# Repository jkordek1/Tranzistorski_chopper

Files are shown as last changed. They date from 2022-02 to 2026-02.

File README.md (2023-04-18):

# Tranzistorski_chopper


[]()



## O projektu
 Tranzistorski chopper korišten za laboratorijske vježbe na elektrotehničkom odjelu TVZ-a.
 
 ## Značajke
 - Ulazni napon do 24V
 - Potenciometar za promjenu širine impulsa visokog stanja PWM-a
 - Ušice za sonde osciloskopa
 - 3 različite frekvencije PWM-a koje se odabiru pomoću kratkospojnika
 
 ## Slike
<p align="center">
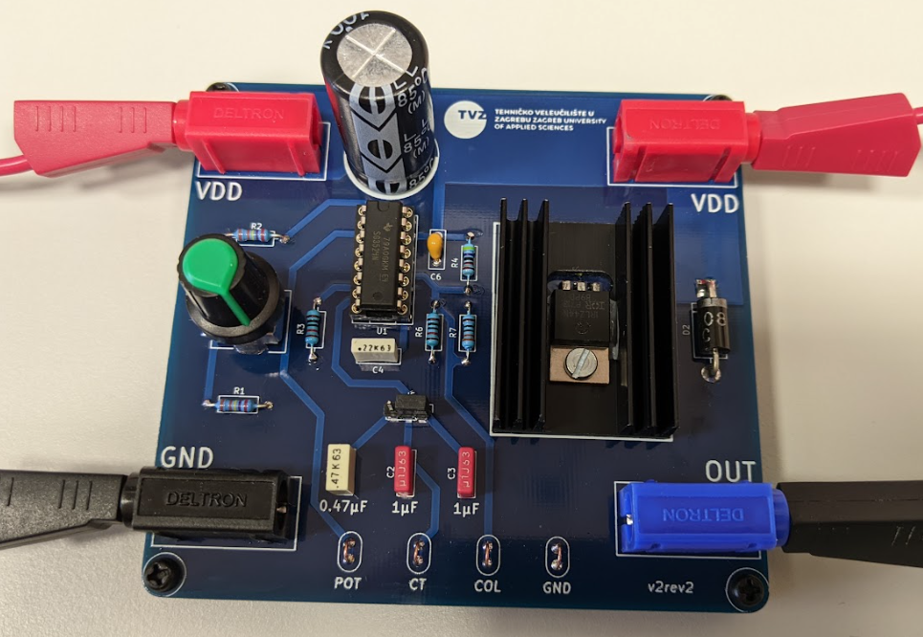
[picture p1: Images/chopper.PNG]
 
</p>

## Struktura mape
    .
    ├── ...
    ├── 3d modeli               # 3d modeli komponenata
    ├── Images                  # Slike i grafički elementi dodani na pločicu
    ├── KiCad files             # Glavna mapa KiCAD projekta
    │   ├── Board2Pdf           # Montažna shema
    │   ├── bom                 # ibom pomoćna datoteka za montažu komponenata
    │   ├── Dokumentacija       # Električna shema
    │   ├── gerber              # gerber mapa
    │   └── Slike               # 3D render sklopa
    └── ...

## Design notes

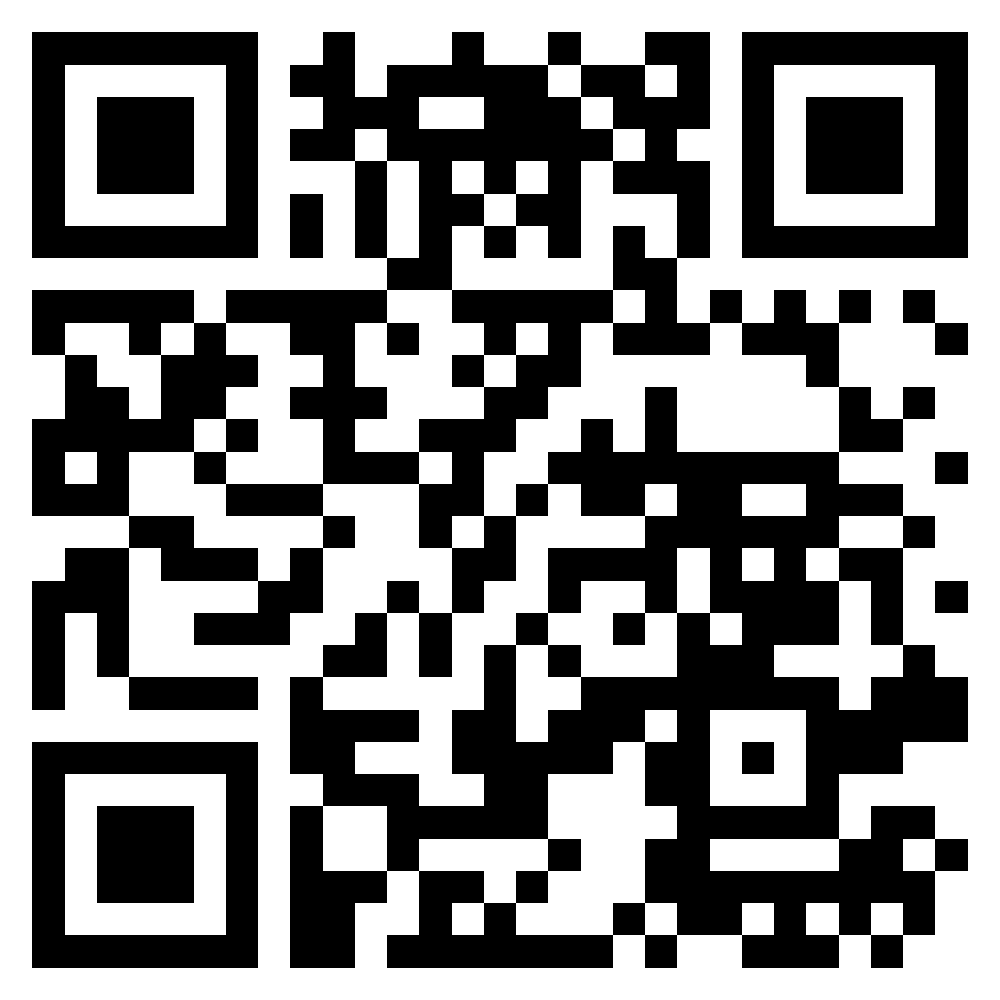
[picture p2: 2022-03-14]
Images/qr.png

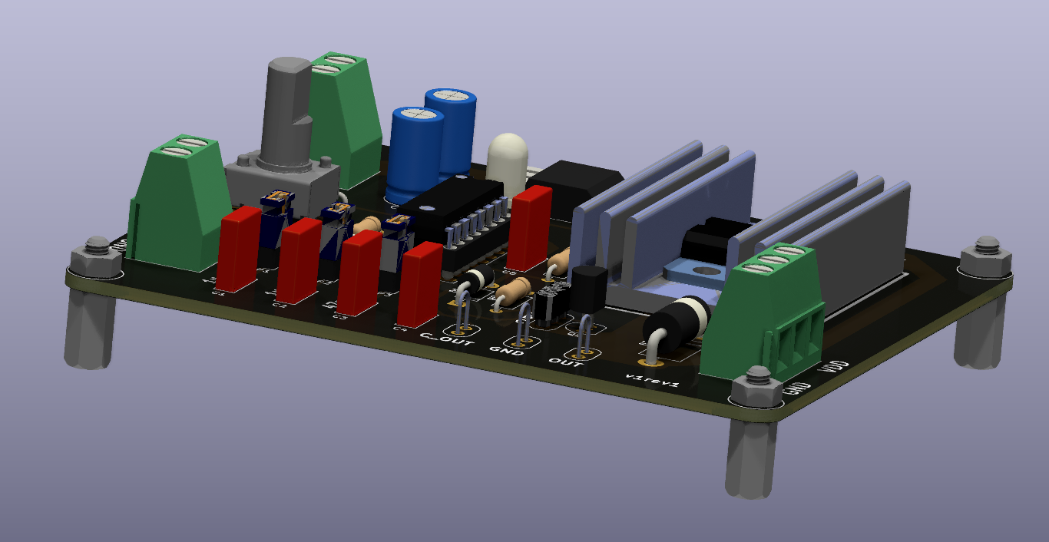
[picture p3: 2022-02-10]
KiCad files/Slike/render.PNG

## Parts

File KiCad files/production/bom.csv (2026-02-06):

Designator | Footprint | Quantity | Value | LCSC Part #
B1, B3 | DELTRON 4mm banana socket - red | 2 | Screw_Terminal_01x01
B2, B4 | DELTRON 4mm banana socket - black | 2 | Screw_Terminal_01x01
C1 | C_Rect_L7.2mm_W2.5mm_P5.00mm_FKS2_FKP2_MKS2_MKP2 | 1 | 1uF
C2 | C_Rect_L7.2mm_W2.5mm_P5.00mm_FKS2_FKP2_MKS2_MKP2 | 1 | 0.47uF
C3 | C_Rect_L7.2mm_W2.5mm_P5.00mm_FKS2_FKP2_MKS2_MKP2 | 1 | 0.22uF
C4 | C_Rect_L7.2mm_W2.5mm_P5.00mm_FKS2_FKP2_MKS2_MKP2 | 1 | 220n
C5 | CP_Radial_D17.0mm_P7.50mm | 1 | 1000u
C6 | C_Rect_L7.2mm_W2.5mm_P5.00mm_FKS2_FKP2_MKS2_MKP2 | 1 | 100n
D2 | D_DO-201AD_P15.24mm_Horizontal | 1 | 1N5408
H1, H2, H3, H4 | MountingHole_3.2mm_M3 | 4 | MountingHole
J1, J2, J3, J4 | oscil | 4 | Conn_01x01_Male
J5 | PinHeader_1x03_P2.54mm_Vertical | 1 | Conn_01x03_Male
Q1 | TO-220F-3_Horizontal_TabDown | 1 | IRFZ44N
R1 | R_Axial_DIN0207_L6.3mm_D2.5mm_P10.16mm_Horizontal | 1 | 3k3
R2 | R_Axial_DIN0207_L6.3mm_D2.5mm_P10.16mm_Horizontal | 1 | 4k7
R3 | R_Axial_DIN0207_L6.3mm_D2.5mm_P10.16mm_Horizontal | 1 | 2k2
R4, R6 | R_Axial_DIN0207_L6.3mm_D2.5mm_P10.16mm_Horizontal | 2 | 10k
R7 | R_Axial_DIN0207_L6.3mm_D2.5mm_P10.16mm_Horizontal | 1 | 330
RV1 | PTV09A-4225F-B502 | 1 | 10k
U1 | DIP-16_W7.62mm_Socket_LongPads | 1 | SG3524

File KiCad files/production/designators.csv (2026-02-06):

B1:1
B2:1
B3:1
B4:1
C1:1
C2:1
C3:1
C4:1
C5:1
C6:1
D2:1
G***:3
H1:1
H2:1
H3:1
H4:1
J1:1
J2:1
J3:1
J4:1
J5:1
Q1:1
R1:1
R2:1
R3:1
R4:1
R6:1
R7:1
RV1:1
U1:1

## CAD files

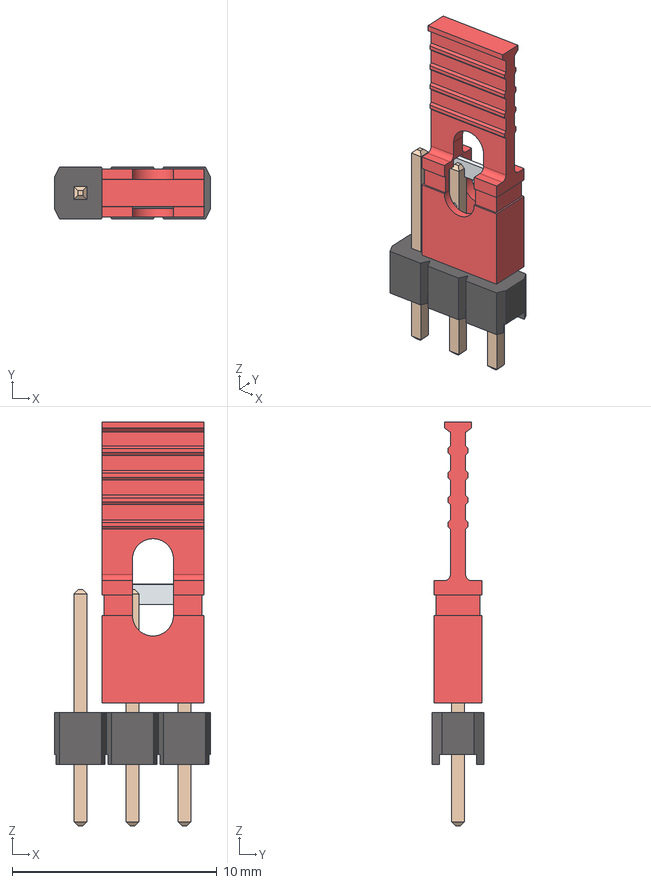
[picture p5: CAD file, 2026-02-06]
3d modeli/pinheader 1x3 and 1 jumper pullback.stp
7.62 x 2.54 x 19.7 mm

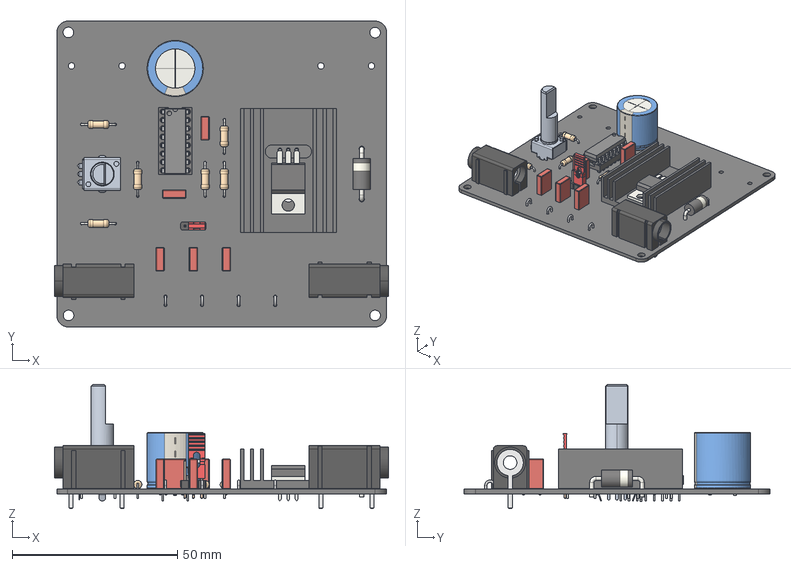
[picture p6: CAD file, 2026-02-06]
KiCad files/Tranzistorski_pretvarač.step
101.1 x 92.6 x 37.5 mm
R_Axial_DIN0207_L6.3mm_D2.5mm_P10.16mm_Horizontal x 6
C_Rect_L7.2mm_W2.5mm_P5.00mm_FKS2_FKP2_MKS2_MKP2 x 5
AB2_90DEG_4MM_JACK_PTH-BLK x 2
AB2_90DEG_4MM_JACK_PTH-RED x 2
Tranzistorski_pretvara_ 1.7.1
usica x 4
D_DO-201AD_P15.24mm_Horizontal
TO-220-3_Horizontal_TabDown
Hladnjak
CP_Radial_D17.0mm_P7.50mm
pinheader 1x3 and 1 jumper pullback
DIP-16_W7.62mm_Socket
DIP-16 N
Tranzistorski_pretvaraÄ_PCB

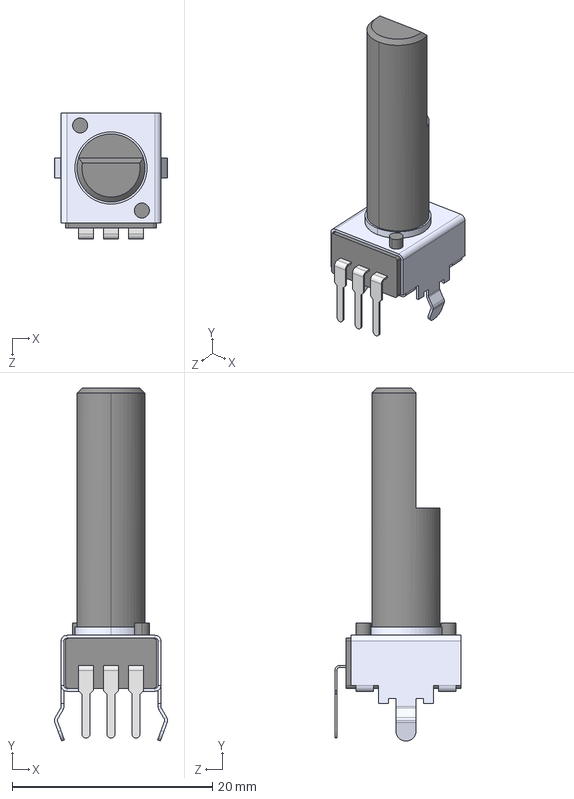
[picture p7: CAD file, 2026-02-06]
3d modeli/PTV09A-4.STEP
11.3 x 35.3 x 12.6 mm
______1.STEP
______2.STEP
______3.STEP

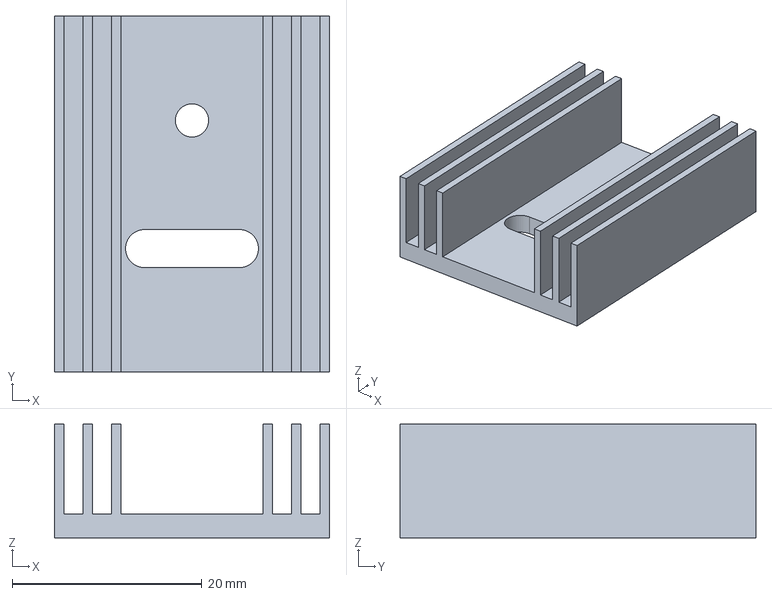
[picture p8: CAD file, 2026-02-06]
3d modeli/Hladnjak.step
29.0 x 37.5 x 12.0 mm

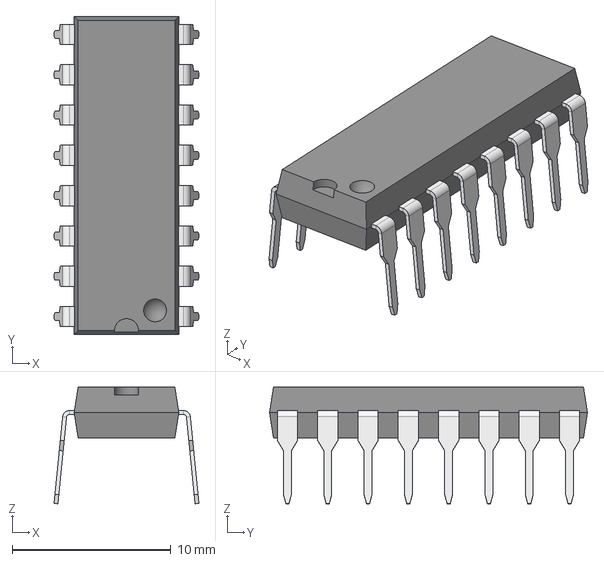
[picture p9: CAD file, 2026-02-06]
3d modeli/DIP-16 N.step
9.14 x 20.0 x 7.35 mm

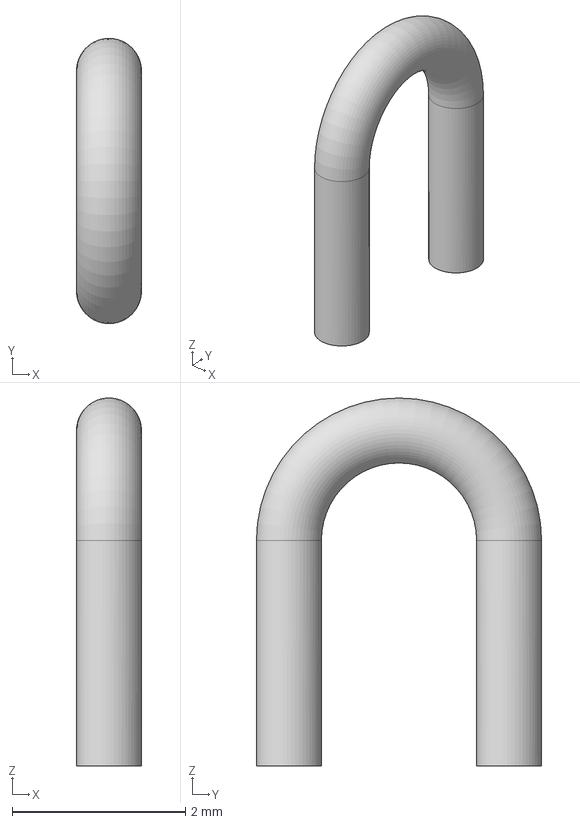
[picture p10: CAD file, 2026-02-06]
3d modeli/usica.step
0.75 x 3.29 x 4.24 mm

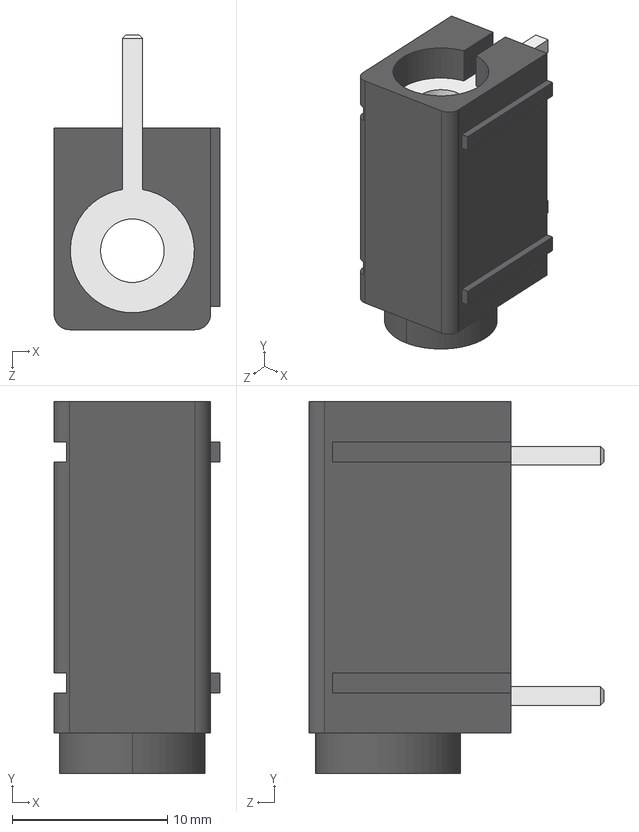
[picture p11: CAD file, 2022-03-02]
3d modeli/AB2_90DEG_4MM_JACK_PTH-BLK.STEP
10.7 x 24.0 x 19.0 mm

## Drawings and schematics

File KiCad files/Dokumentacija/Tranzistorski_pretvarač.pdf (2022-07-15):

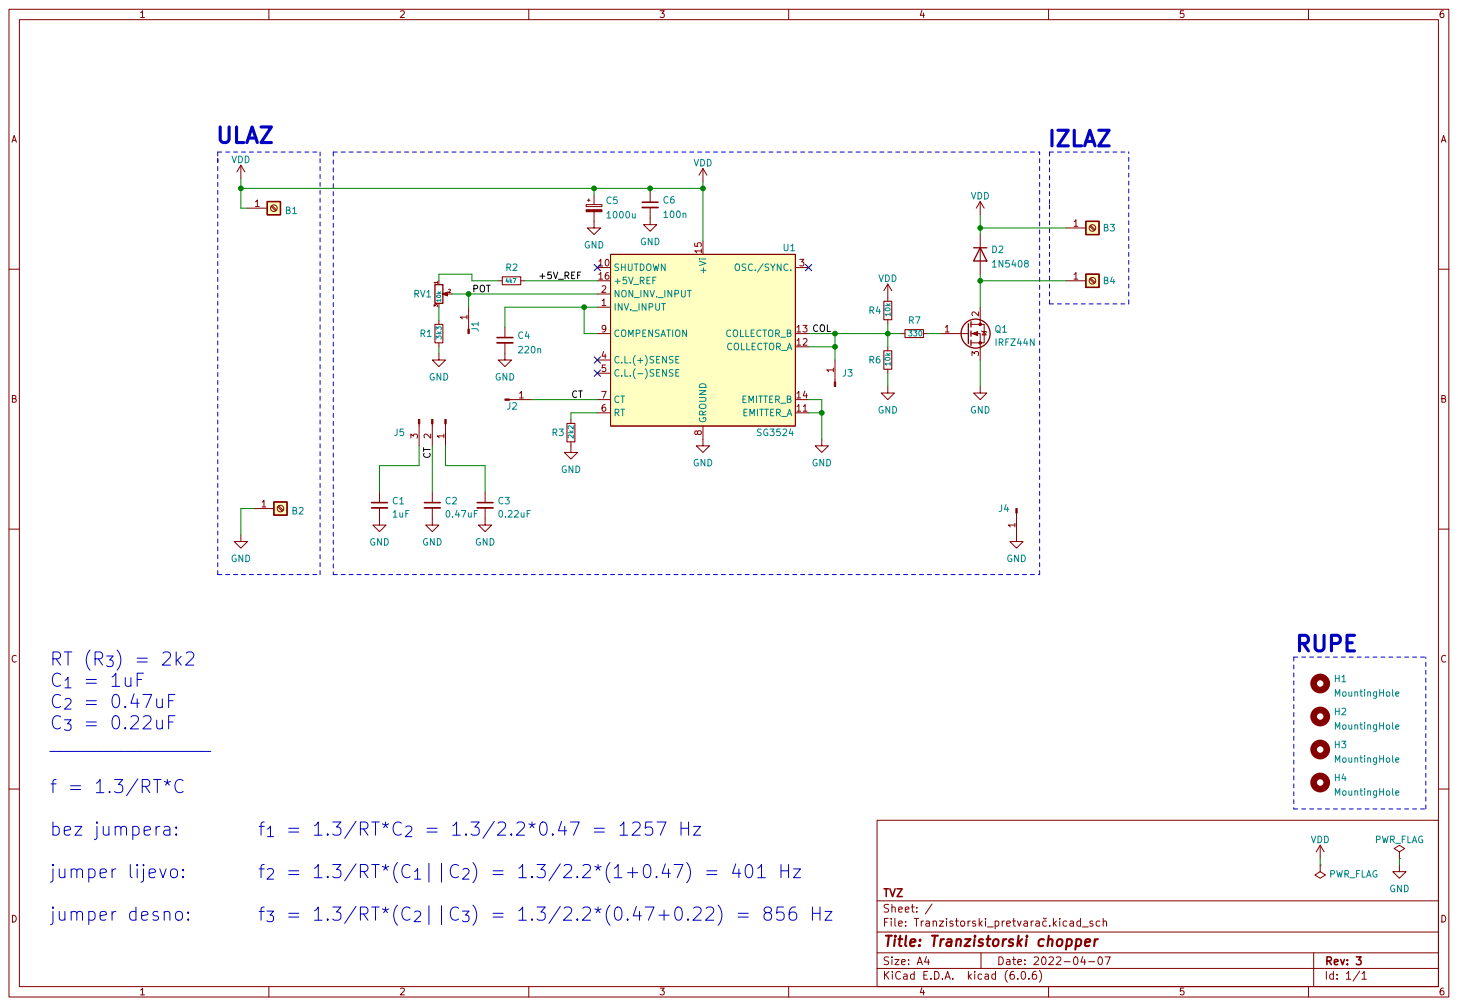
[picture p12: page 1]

bez jumpera: f_{1} = 1.3/RT*C_{2} = 1.3/2.2*0.47 = 1257 Hz

jumper lijevo: f_{2} = 1.3/RT*(C_{1}||C_{2}) = 1.3/2.2*(1+0.47) = 401 Hz

jumper desno: f_{3} = 1.3/RT*(C_{2}||C_{3}) = 1.3/2.2*(0.47+0.22) = 856 Hz

Id: 1/1 Title: Tranzistorski chopper

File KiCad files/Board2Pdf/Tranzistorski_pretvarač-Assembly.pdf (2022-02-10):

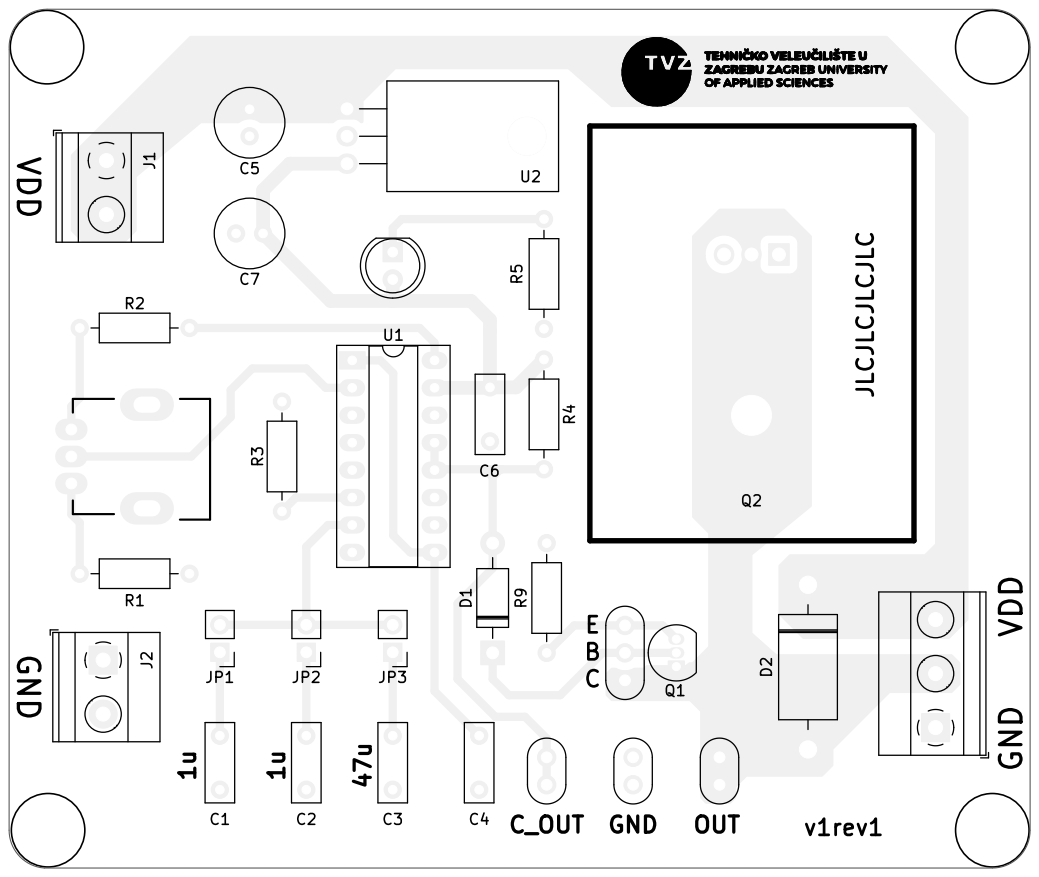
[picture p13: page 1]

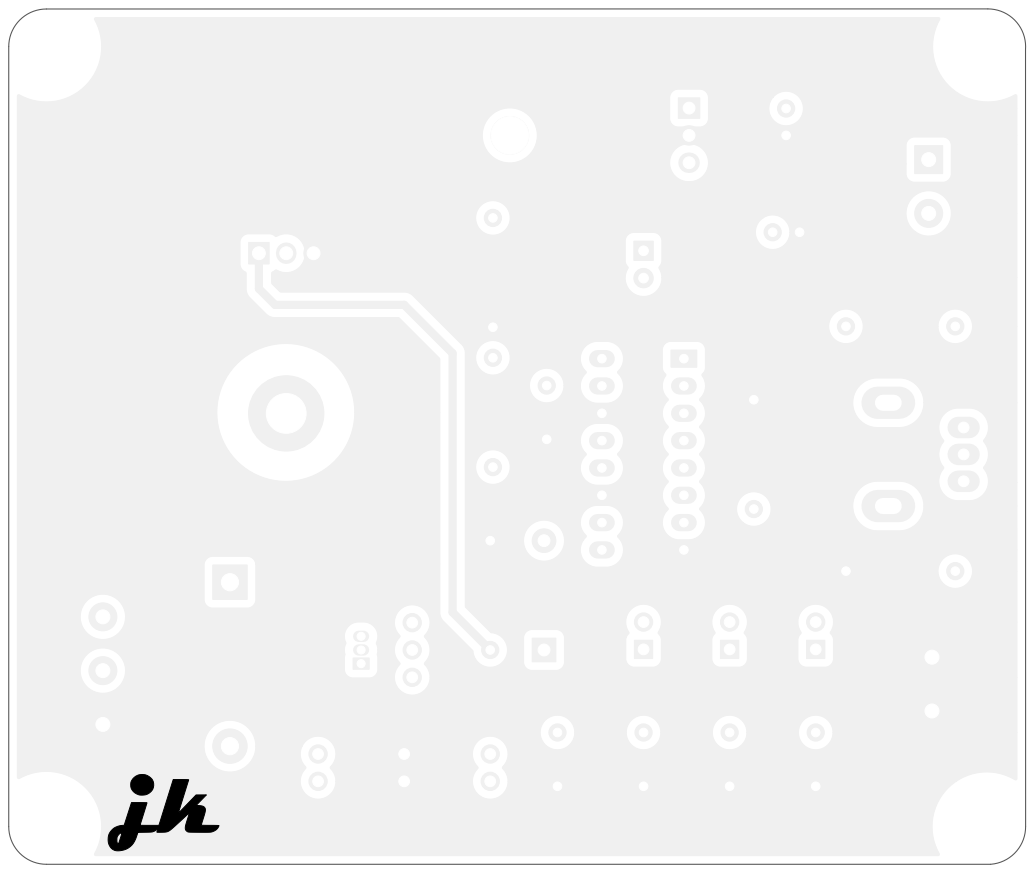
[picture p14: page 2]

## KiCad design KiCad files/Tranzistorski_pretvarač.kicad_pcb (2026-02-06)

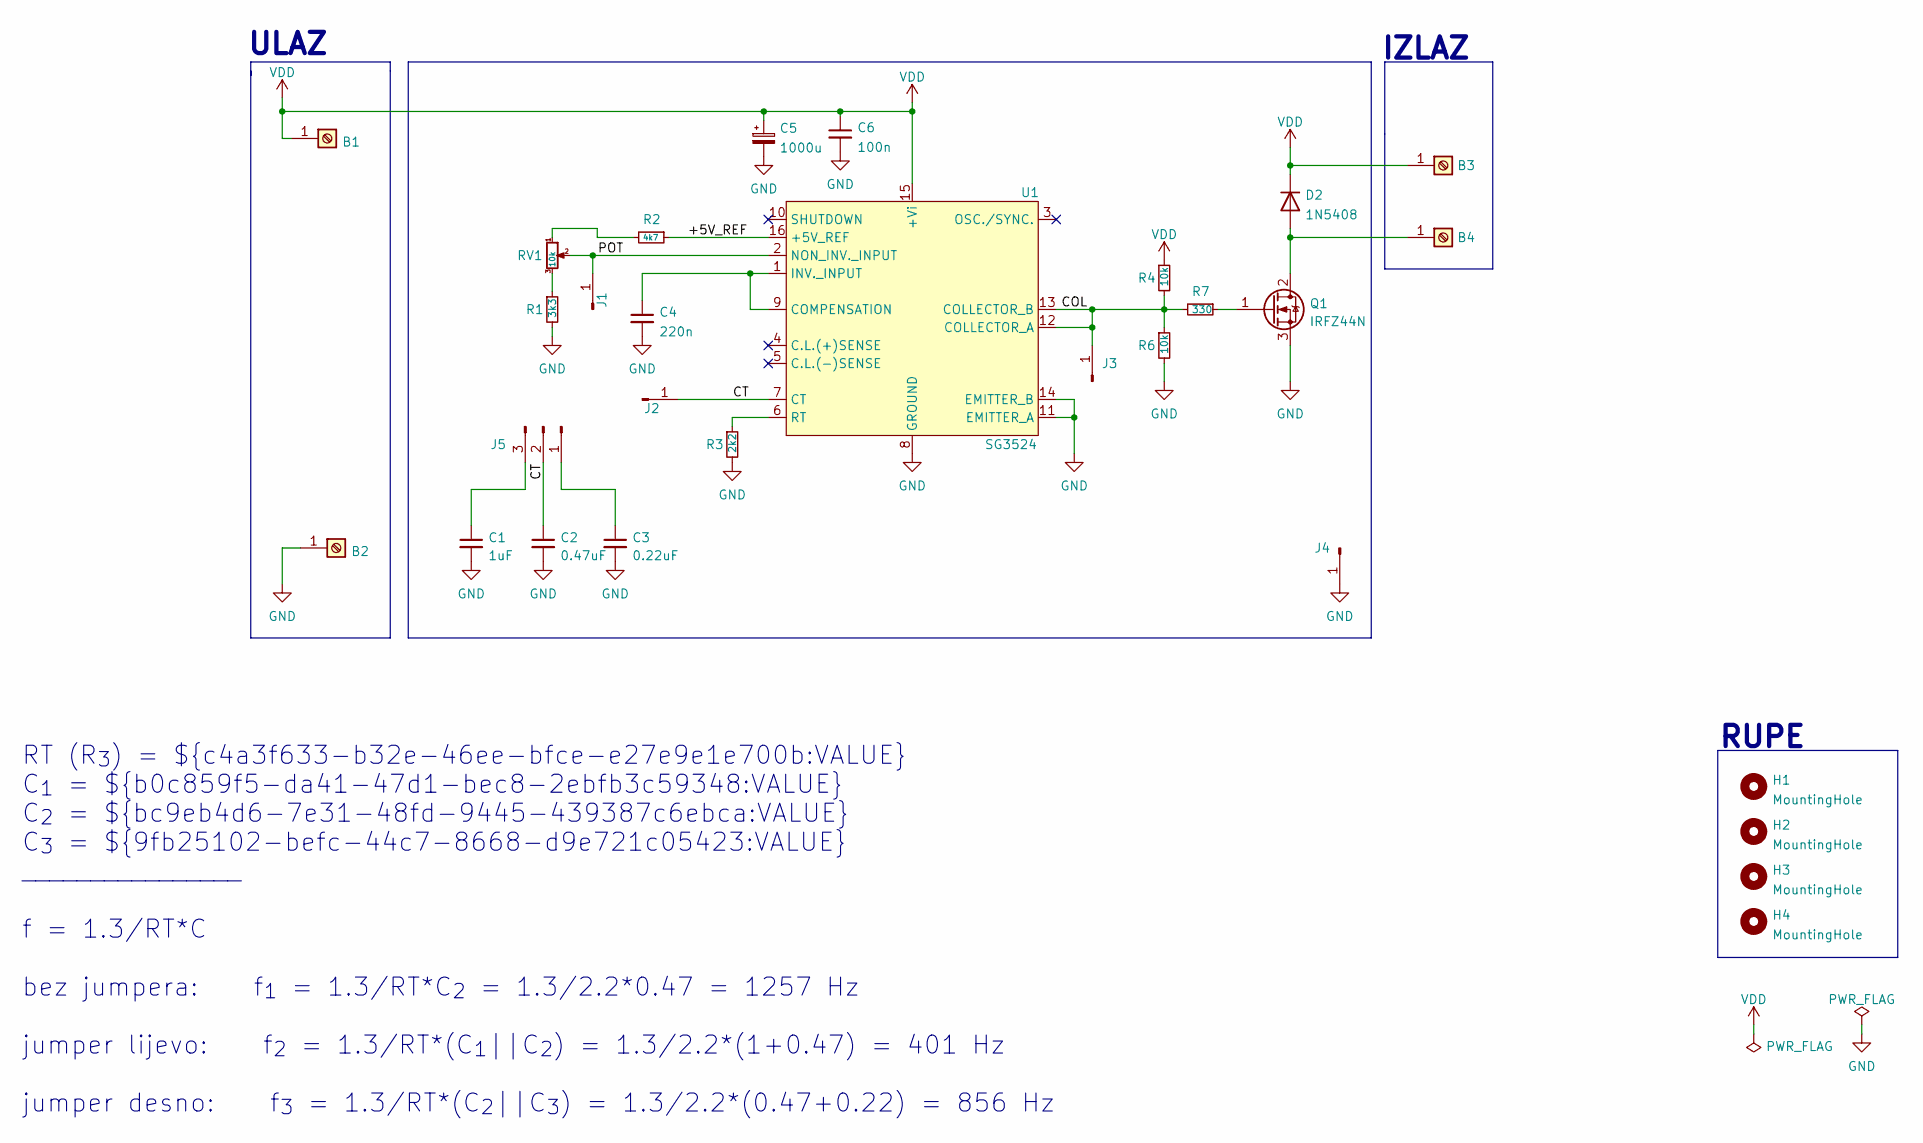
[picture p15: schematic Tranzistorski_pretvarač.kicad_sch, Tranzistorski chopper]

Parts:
B1, B3: Screw_Terminal_01x01; DELTRON 4mm banana socket - red
B2, B4: Screw_Terminal_01x01; DELTRON 4mm banana socket - black
C1: 1uF; C_Rect_L7.2mm_W2.5mm_P5.00mm_FKS2_FKP2_MKS2_MKP2
C2: 0.47uF; C_Rect_L7.2mm_W2.5mm_P5.00mm_FKS2_FKP2_MKS2_MKP2
C3: 0.22uF; C_Rect_L7.2mm_W2.5mm_P5.00mm_FKS2_FKP2_MKS2_MKP2
C4: 220n; C_Rect_L7.2mm_W2.5mm_P5.00mm_FKS2_FKP2_MKS2_MKP2
C5: 1000u; CP_Radial_D17.0mm_P7.50mm
C6: 100n; C_Rect_L7.2mm_W2.5mm_P5.00mm_FKS2_FKP2_MKS2_MKP2
D2: 1N5408; D_DO-201AD_P15.24mm_Horizontal
H1, H2, H3, H4: MountingHole; MountingHole_3.2mm_M3
J1, J2, J3, J4: Conn_01x01_Male; oscil
J5: Conn_01x03_Male; PinHeader_1x03_P2.54mm_Vertical
Q1: IRFZ44N; TO-220F-3_Horizontal_TabDown
R1: 3k3; R_Axial_DIN0207_L6.3mm_D2.5mm_P10.16mm_Horizontal
R2: 4k7; R_Axial_DIN0207_L6.3mm_D2.5mm_P10.16mm_Horizontal
R3: 2k2; R_Axial_DIN0207_L6.3mm_D2.5mm_P10.16mm_Horizontal
R4, R6: 10k; R_Axial_DIN0207_L6.3mm_D2.5mm_P10.16mm_Horizontal
R7: 330; R_Axial_DIN0207_L6.3mm_D2.5mm_P10.16mm_Horizontal
RV1: 10k; PTV09A-4225F-B502
U1: SG3524; DIP-16_W7.62mm_Socket_LongPads

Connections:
/+5V_REF: R2.1, U1.16 (+5V_REF)
/COL: J3.1, R4.2, R6.1, R7.2, U1.12 (COLLECTOR_A), U1.13 (COLLECTOR_B)
/CT: C2.1, J2.1, J5.2, U1.7 (CT)
/POT: J1.1, RV1.2, U1.2 (NON_INV._INPUT)
GND: B2.1, C1.2, C2.2, C3.2, C4.2, C5.2, C6.2, J4.1, Q1.3 (S), R1.2, R3.2, R6.2, U1.8 (GROUND), U1.11 (EMITTER_A), U1.14 (EMITTER_B)
unnamed: B4.1, D2.2 (A), Q1.2 (D)
unnamed: C1.1, J5.3
unnamed: C3.1, J5.1
unnamed: C4.1, U1.1 (INV._INPUT), U1.9 (COMPENSATION)
unnamed: Q1.1 (G), R7.1
unnamed: R1.1, RV1.3
unnamed: R2.2, RV1.1
unnamed: R3.1, U1.6 (RT)
VDD: B1.1, B3.1, C5.1, C6.1, D2.1 (K), R4.1, U1.15 (+Vi)

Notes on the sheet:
RUPE
IZLAZ
ULAZ
RT (R_{3}) = ${c4a3f633-b32e-46ee-bfce-e27e9e1e700b:VALUE} C_{1} = ${b0c859f5-da41-47d1-bec8-2ebfb3c59348:VALUE} C_{2} = ${bc9eb4d6-7e31-48fd-9445-439387c6ebca:VALUE} C_{3} = ${9fb25102-befc-44c7-8668-d9e721c05423:VALUE} ________________ f = 1.3/RT*C bez jumpera: f_{1} = 1.3/RT*C_{2} = 1.3/2.2*0.47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

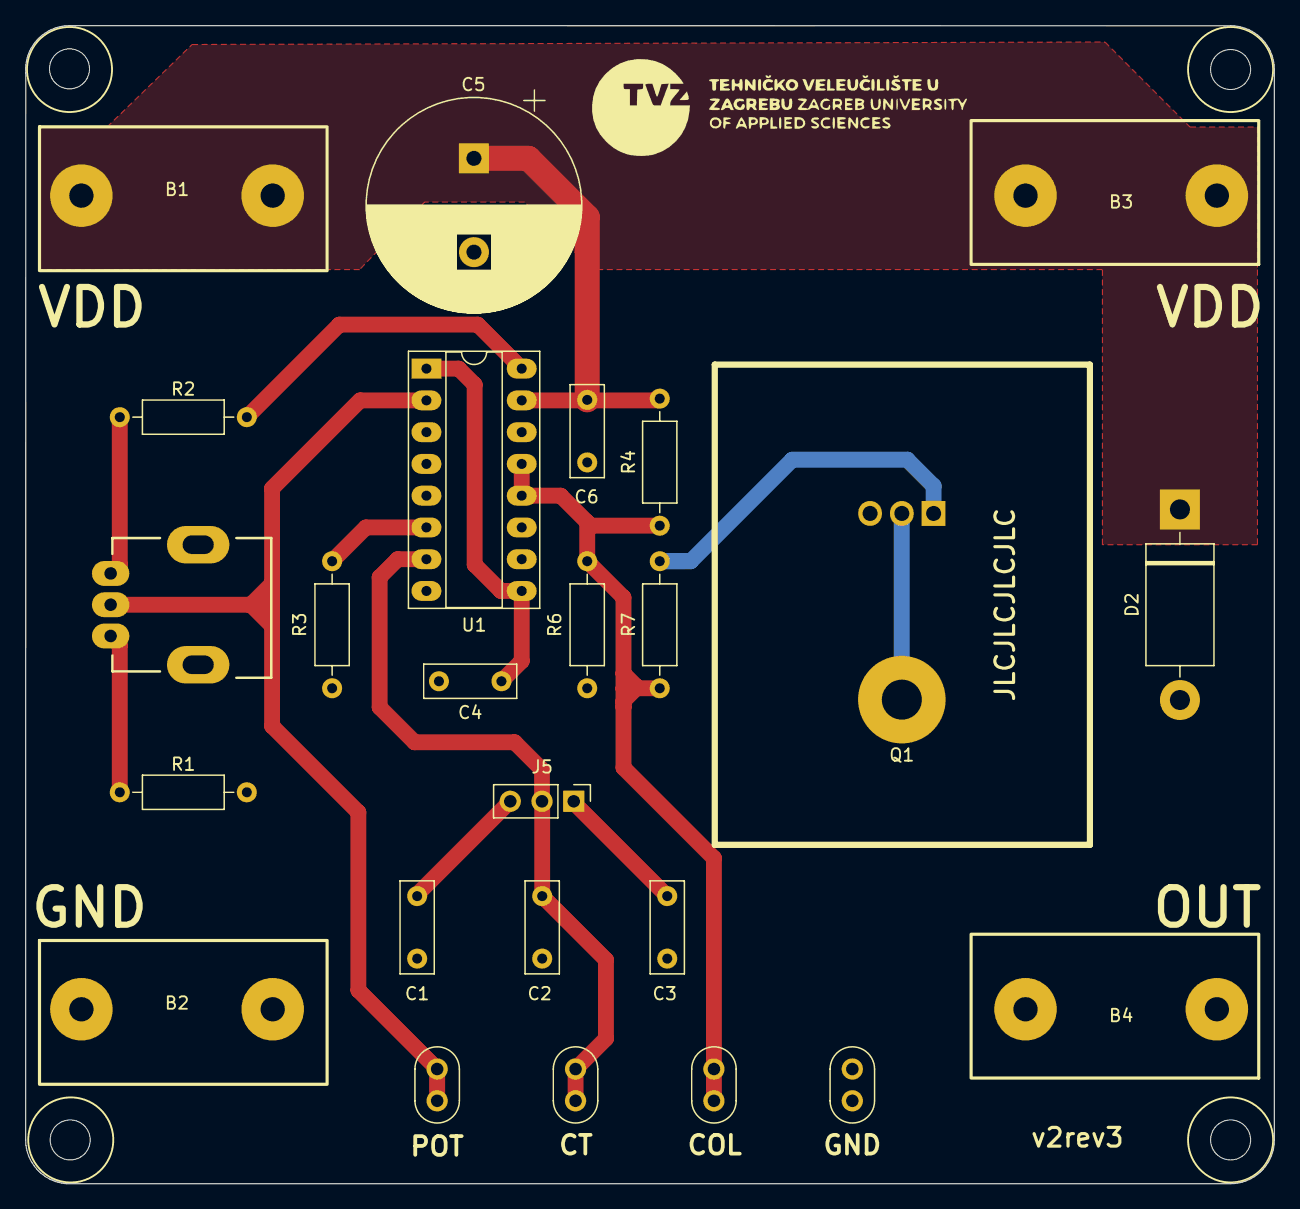
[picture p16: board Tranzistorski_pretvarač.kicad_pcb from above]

Board: 2 copper layers, 99.9 x 92.6 mm, 29 parts (0 on the bottom side), 14 nets.

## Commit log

2022-02-10 bulk cap
    [Tranzistorski_pretvarač.kicad_sch]
2022-02-12 added probe
    [Tranzistorski_pretvarač-B_Cu.gbr, Tranzistorski_pretvarač-B_Mask.gbr, Tranzistorski_pretvarač-B_Paste.gbr, Tranzistorski_pretvarač-B_Silkscreen.gbr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]
2022-02-22 shema update
    [Tranzistorski_pretvarač.kicad_sch]
2022-03-14 qr code
    [Tranzistorski_pretvarač-B_Cu.gbr, Tranzistorski_pretvarač-B_Mask.gbr, Tranzistorski_pretvarač-B_Paste.gbr, Tranzistorski_pretvarač-B_Silkscreen.gbr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]
2022-03-14 remove copper
    [Tranzistorski_pretvarač-B_Cu.gbr, Tranzistorski_pretvarač-B_Mask.gbr, Tranzistorski_pretvarač-B_Paste.gbr, Tranzistorski_pretvarač-B_Silkscreen.gbr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]
2022-04-11 generate documentation
    [Tranzistorski_pretvarač-B_Cu.gbr, Tranzistorski_pretvarač-B_Mask.gbr, Tranzistorski_pretvarač-B_Paste.gbr, Tranzistorski_pretvarač-B_Silkscreen.gbr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]
